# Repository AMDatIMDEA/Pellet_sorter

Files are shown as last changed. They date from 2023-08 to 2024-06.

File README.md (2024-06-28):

# Pellet distributor
CAD and Arduino/Python code files for the pellet distributor robot developed at the Accelerated Materials Discovery group from IMDEA Materials.

A tutorial for using the code is available as a [Notebook](Code/Python/Pellet_distributor_py/Example_using_pellet_distributor.ipynb)

⚠ All parts are designed to be printed, if possible, according to the specified [Cura settings](Resources/Ultimaker_S5_Cura_Config.curaprofile). These include:
- Horizontal Expansion: -0.1 mm
- Initial Layer Horizontal Expansion: -0.16 mm

## Introduction to the project & current state
The pellet distributor robot is a double-jointed articulated tube designed for pellets to be distributed into a set of cups on a tray, with the aim of automating the output of the material production process:
> Mixing of desired composition 🠚 Extrusion 🠚 Cooling 🠚 Pelletizing 🠚 **SORTING** ⇨ Transport to sample manufacture & experimentation

The parts, designed in FreeCAD, are made mostly of PLA by 3D printing, together with 50mm diameter PVC pipe sections, and nuts and bolts for fastening. The robot, measuring 552x497x236mm, uses two stepper motors for positioning, one on its base and another closer to the end of the arm, allowing it to effectively sweep a truncated circular sector below the pelletizer that covers the entire area of a tray. A third stepper actuates the opening and closing of a butterfly valve.  The whole assembly is suspended beneath the pelletizer by two arms on the top funnel/hopper, inserted into aluminum railings just under where the pellets exit. These make their way through the first joint, the valve (if open), and through the second joint, before reaching the nozzle and dropping into a cup or being discarded. The tray holding the cups is set up on a scale, which enables the control of fill levels of cups, as well as determining the material yield.

The motors are controled by A4988 drivers and an Arduino Uno R3 board, which is in turn managed by a Python script on a computer. The communication between these is established through a serial protocol, hence the Arduino must be plugged in by USB during operation, in addition to the power cable for the motors. The scale is also connected by its own serial port to the script. This Python code makes use of the Inverse Kinematics Python library (IKPy), through which the number of steps that each motor needs to take can be calculated in order for the robot to move its nozzle to a desired position. This versatility in the code, together with the fact that the arm should be able to reach any point within the swept region defined above, implies that the design is theoretically adaptable to any tray and cup arrangement, as long as these fit within said area.

The way the current script works is the following: Firstly, the robot arm must be pointing completely straight and perpendicular to the face of the pelletizer, and the current 9-hole square tray, whose center is alligned with the axis of rotation of the bottom joint, is set up on the scale. Then, the scale is zeroed, the arm rotates to the first cup's coordinates, opens the valve and lets pellets through. Once the predetermined weight capacity of each cup is reached, as measured on the scale, the script knows to close the valve and move on to the next cup. It does this rotating through all 8 external cups, then finally goeas to the center cup. Once this one has been filled it returns to the initial position.

The following items are currently hard-coded into the script, hence they are accounted for but require user input if change is needed:
- Initial position of the robot arm's tip
- Position of the tray relative to the robot
- Position of each cup relative to the tray
- Occupancy state of the tray slots
- Cup fill level, material, and other properties

However, the following are addressed dynamicaly, and therefore would require no adaptation in case of future tray design and operation changes:
- Path to take in between coordinates
- Operation of the valve
- Operation of the scale
- The Arduino code as a whole

## Current issues and future development
There are, however, to problems that have been encountered with this design. First, the flexing of the mounting bracket of the top stepper motor, together with the fact that the top joint is driven by a gear train instead of a belt mechanism, means that during translation of the top arm (which currently only occurs for the 9th cup) the gears can be pushed appart under torque and disengaged by the flexing, resulting in missed rotation. Note that, since there is no feedback through the motors themselves nor through an external system such as CV, the script has no way of accounting for missed steps, or, as is the case here, a disengagement of the gear train, hence it can be mistaken about the real location of the nozzle.

A second issue is static charge. It appears that most stages of the material production process can induce it: the extrusion by the fillament rubbing at the exit; the cooling channel again by triboelectric effect due to the air sprayed over the fillament; the pelletizer also by contact, with the rollers or the casing; and even perhaps the robot tube itself once the pellets are cut, since they slide over the plastic surface. This causes problems since it allows for two things to happen: the pellets might get stuck in the tube due to attraction to the walls; and, once a cup reaches a certain fill level, the charged pellets within it act as an electric repulsor for oncoming pelles (since they all hold the same charge), pushing them away from falling into the cup and in some instances making them fly out of the cup rather dramatically. I believe that simply discharging the pellets, as has been attempted, is not a sufficient fix since they might be attracted to the discharge points (Eg: aluminum foil), creating an insulating barrier through which the rest of the pellets cannot lose their charge, hence the problem remains. The current consideration is using ionized air, as appears to be the industry consensus, to remove the pellets charge.

In light of these hurdles, and keeping the ambitions of the whole RobotLab in mind, there are some suggestions to be made for future developments regarding this project:
- Implementing Computer Vision (CV), for direct object detection as well as asisted, for instance, through ArUco markers. This could enable:
  - Knowledge of the tray's exact coordinates, removing the need for precise alignment when placing it under the robot.
  - Determining the location of each cup individually, instead of having to hard-code their coordinates relative to the tray for each existing tray design.
  - Detecting the state of the cups, such as their fill level; or if there is a problem, so that they can be skipped (Eg: Cup missing, already full, contaminated or partially containing a material different than the one currently being extruded)
  - Interaction with a separate robotic arm, that can pick up the cups and/or trays after they have been filled.
  - Vissual feedback on the robot arm's pose, which eliminates missmatch issues between the real pose and the ideal one.
- Creating a database that, interacting with the script, can cataloge the available trays, those in storage; the contents, fill level,s and properties of every cup, etc. This would be necessity if there ever is the desire to scale production, and would be useful for the transport system to interact with.

And some less impactful TO-DOs:
- Implementing tray swapping into the script, so that after operation it holds the valve closed in the initial position while a human/robot picks up the full tray and swaps in a new, empty one. This could be done either with a simple user input through consol, which would replace restarting the script, or even in a more automatic fashion by using the scale to detect negative weight when the tray has been taken out, then waiting for a slight increase corresponding to the new empty tray being placed.
- Vertically integrating the script upwards with an overarching material production control script, that manages the mixing, extrusion and pelletizing. This would not be too difficult given how the robot operation is built on a functional basis, and the management of cups and trays is object-oriented.

[> Back to top](#TOP)

## Useful links & references

- [ ] [Arduino & Breadboard wiring diagram](https://github.com/AMDatIMDEA/Pellet_sorter/blob/3199d7dc5ab3ea5f197367ed4c28cb93c2f82943/Schematics/Electronics/Pellet%20Sorter%20Arduino%20and%20Driver%20Wiring%20Drawing%20Final%20Annotated.png)

### ⚡ Stepper Motors
- [Arduino AccelStepper Class Reference](https://www.airspayce.com/mikem/arduino/AccelStepper/classAccelStepper.html)
- [Arduino AccelStepper Examples](https://www.airspayce.com/mikem/arduino/AccelStepper/examples.html)
- [A4988 Driver simplified guide](https://lastminuteengineers.com/a4988-stepper-motor-driver-arduino-tutorial/)
- [ ] [Small stepper datasheet](https://github.com/AMDatIMDEA/Pellet_sorter/blob/d0cadbf57e2ab080da146999fbca15fec0f52def/Resources/Guides_and_Datasheets/290-028-1_ts-24byj48a-25-pxw%20Stepper.pdf)
- [ ] [SX-NEMA17 Stepper datasheet](https://github.com/AMDatIMDEA/Pellet_sorter/blob/d0cadbf57e2ab080da146999fbca15fec0f52def/Resources/Guides_and_Datasheets/SX17%20NEMA17%20Stepper.pdf)
- [ ] [A4998 Driver datasheet](https://github.com/AMDatIMDEA/Pellet_sorter/blob/d0cadbf57e2ab080da146999fbca15fec0f52def/Resources/Guides_and_Datasheets/A4988-%20Driver%20Datasheet.pdf)

### 🔌 Serial port
- [Arduino Serial functions](https://www.arduino.cc/reference/en/language/functions/communication/serial/)
- [Python pySerial API Classes](https://pyserial.readthedocs.io/en/latest/pyserial_api.html)

### ⛓ Inverse Kinematics
- [IKPy GitHub Repo](https://github.com/Phylliade/ikpy)
- [IKPy Documentation](https://ikpy.readthedocs.io/en/latest/ikpy.html)

### ⚖ Balance
- [ ] [CPWplus Scale datasheet](https://github.com/AMDatIMDEA/Pellet_sorter/blob/d0cadbf57e2ab080da146999fbca15fec0f52def/Resources/Guides_and_Datasheets/CPWplus_UM_USA%20Scale.pdf)

### 🐢 TurtleBot
- [TurtleBot 4 GitHub Hardware repo](https://github.com/turtlebot/turtlebot4-hardware/tree/master/TurtleBot%204/Components)
- [ ] [TurtleBot 4 Integration Platform datasheet](https://github.com/AMDatIMDEA/Pellet_sorter/blob/c34230bc0438fd95317bfee5fad6f5a7074d98d1/Resources/Guides_and_Datasheets/TurtleBot%20Top%20Integration%20platform%20draft.pdf)

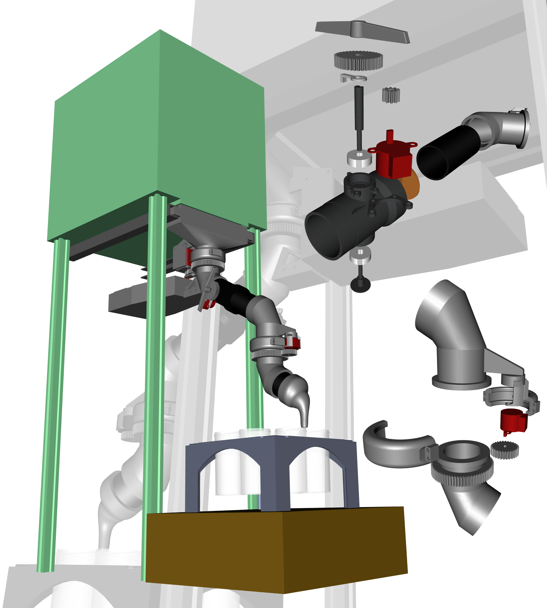
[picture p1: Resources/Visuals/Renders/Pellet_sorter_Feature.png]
Pellet sorter rendering


[> Back to top](#TOP)

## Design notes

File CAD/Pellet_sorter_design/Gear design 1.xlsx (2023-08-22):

Small stepper |  |  |  |  |  |  |  | SX17 Stepper |  |  |  |  |  |  |  | Small stepper
Module | m | 1.5 | mm |  |  |  |  | Module | m | 1.5 | mm |  |  |  |  | Module | m | 1 | mm
# Teeth G | N_G | 48 | - | Diam. G | d_G | 72 | mm | # Teeth G | N_G | 48 | - | Diam. G | d_G | 72 | mm | # Teeth G | N_G | 39 | - | Diam. G | d_G | 39 | mm
# Teeth p | N_p | 20 | - | Diam. P | d_p | 30 | mm | # Teeth p | N_p | 42 | - | Diam. P | d_p | 63 | mm | # Teeth p | N_p | 10 | - | Diam. P | d_p | 10 | mm
Ratio | i | 2.4 | - | C2C dist. | C | 51 | mm | Ratio | i | 1.142857143 | - | C2C dist. | C | 67.5 | mm | Ratio | i | 3.9 | - | C2C dist. | C | 24.5 | mm
 |  |  |  |  |  |  |  |  |  |  |  |  |  |  |  |  |  |  |  |  |  | 24.4658
 |  |  |  |  |  |  |  |  |  |  |  |  |  |  |  |  |  |  |  |  | Rescale | 0.9986040816
 |  |  |  |  |  |  |  |  |  |  |  |  |  |  |  | 0.9986040816
 |  |  |  |  |  |  |  | Scrapped: SX17 Stepper w/Idler
 |  |  |  |  |  |  |  | Module | m | 1.5 | mm
 |  |  |  |  |  |  |  | # Teeth G | N_G | 48 | - | Diam. G | d_G | 72 | mm
 |  |  |  |  |  |  |  | # Teeth p | N_p | 10 | - | Diam. P | d_p | 15 | mm | Small stepper Chute Joint update
 |  |  |  |  |  |  |  | # Teeth I | N_I | 16 | - | Diam. I | d_I | 24 | mm | Module | m | 1 | mm
 |  |  |  |  |  |  |  |  |  |  |  |  |  |  |  | # Teeth G | N_G | 72 | - | Diam. G | d_G | 72 | mm
 |  |  |  |  |  |  |  |  |  |  |  |  |  |  |  | # Teeth p | N_p | 30 | - | Diam. P | d_p | 30 | mm
 |  |  |  |  |  |  |  | Ratio | i | 4.8 | - | C2C d. GI | C_GI | 48 | mm | Ratio | i | 2.4 | - | C2C dist. | C | 51 | mm
 |  |  |  |  |  |  |  |  |  |  |  | C2C d. Ip | C_Ip | 19.5 | mm
 |  |  |  |  |  |  |  |  |  |  |  | C2C d. tot | C_tot | 67.5 | mm
 |  |  |  |  |  |  |  |  |  |  |  |  |  | 67.5
Top redisign
Module | m | 1 | mm
# Teeth G | N_G | 72 | - | Diam. G | d_G | 72 | mm
# Teeth p | N_p | 12 | - | Diam. P | d_p | 12 | mm
# Teeth I | N_I | 26 | - | Diam. I | d_I | 26 | mm
Ratio | i | 6 | - | C2C d. GI | C_GI | 49 | mm
 |  |  |  | C2C d. Ip | C_Ip | 19 | mm
 |  |  |  | C2C d. tot | C_tot | 68 | mm
 |  |  |  |  |  | 67.5

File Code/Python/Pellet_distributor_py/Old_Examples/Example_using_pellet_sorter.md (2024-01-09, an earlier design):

# Example using pellet sorter

This notebook contains an example of how to run the code for collecting the material. Most cells can be run without any modification if the collector has been built without design modifications. The lines that need modifications are markedlike this:

`###############################################################################################################`

```python
# Import Libraries
import serial
import numpy as np
import time
import os
import serial.tools.list_ports
```

In this cell, we define the port name for the arduino and the balance. We do it by listing the connected ports and selecting the ones whose device serial is the corresponding to our device. You should find the serial of your devices and change it accordingly. You can do it by inspecting the devices detected by serial.tools.list_ports.comports(). In case of doubt, try disconnecting and connecting to see which ports are affected.

```python
ports = serial.tools.list_ports.comports()

###############################################################################################################

arduino_serial = "write_here_your_arduino_serial"
balance_serial = "write_here_your_balance_serial"

###############################################################################################################

for port in ports:
    if port.serial_number == arduino_serial:
        arduino_port = port.device
    elif port.serial_number == balance_serial:
        balance_port = port.device
        
### Serial initialization
## Arduino
arduino = serial.Serial(arduino_port, 9600)
## Balance
balance = serial.Serial(balance_port, 9600)
```

We import the functions from the pellet_sorter.py script. Note: you need to install the `ikpy` library

```python
import pellet_sorter as ps
```

Define the capacity of the cup in kg

```python
###############################################################################################################
cup_capacity = 0.16
###############################################################################################################
```

The next cell defines a series of parameters needed for the calculations. They don't have to be modified unless you have modified something in the design.

```python
### Initializations
# sorter_chain, sorter_parameters and arduino should be global variables

n_joints = 2
sorter_parameters = [{'steps_in_rotation':0,'gear_ratio':0,'length_mm':0,'bound_rad':0, 'cartesian':[0,0]} for k in range(n_joints)]
## Top
sorter_parameters[0]['steps_in_rotation'] = np.round(200*1.1)   # Calibrate multiplicative factor to compensate lost steps if necessary
sorter_parameters[0]['gear_ratio'] = 6
sorter_parameters[0]['length_mm'] = 180.5
sorter_parameters[0]['bound_rad'] = np.deg2rad(35)    # np.deg2rad(35)  # IK Rotation bound in either direction, not total
sorter_parameters[0]['cartesian'] = [sorter_parameters[0].get('length_mm'), 0]
## Bot
sorter_parameters[1]['steps_in_rotation'] = 812
sorter_parameters[1]['gear_ratio'] = 2.4
sorter_parameters[1]['length_mm'] = np.sqrt(32.7**2 + 79.2**2)  # 84.4
sorter_parameters[1]['bound_rad'] = np.deg2rad(10*360)
sorter_parameters[1]['cartesian'] = [sorter_parameters[1].get('length_mm'), 0]

# Positions of the cups in the tray

tray_1 = ps.Tray('1', [sorter_parameters[0]['length_mm'], 0], [
    ps.Slot([79.2,32.7]),
    ps.Slot([32.7,79.2]),
    ps.Slot([-32.7,79.2]),
    ps.Slot([-79.2,32.7]),
    ps.Slot([-79.2,-32.7]),
    ps.Slot([-32.7,-79.2]),
    ps.Slot([32.7,-79.2]),
    ps.Slot([79.2,-32.7]),
    ps.Slot([0,0]), 
    ])

tray_1.fill_all_slots_ez(0, cup_capacity)
tray_1.set_all_material('PLA####')
```

In the next cell, we use the Arduino Command Line Interface (arduino-cli) to compile and upload the arduino script. If you prefer to do it using the Graphical User Interface, skip this cell. For using it, update the location of your arduino-cli

```python
###############################################################################################################

os.system("/PATH/arduino-cli compile --fqbn arduino:avr:uno ../../Arduino/Pellet_sorter_v2/Pellet_sorter_v2.ino")
os.system("/PATH/arduino-cli upload -p "+arduino_port+" --fqbn arduino:avr:uno ../../Arduino/Pellet_sorter_v2/Pellet_sorter_v2.ino")

###############################################################################################################
```

The `fill_tray` function will run all the process. It uses the objects defined in the previous steps. The three parameters that allow interesting customization are: 

`:param seq: List with the order of filling of the cups. If None, they will all be filled in default order`

`:param purge_slot: Number of the slot used for purging. This slot can be left without cup so the material is discarded. Used when changing material. If None, no purging will be done.`
                        
`:param purge_time: Time for purge in minutes. Default: 0`

If `seq = None` and `purge_slot = None`, the cups will be filled sequentially (from 0 to 8) without any purging.

If `purge_slot` is not None, like `purge_slot = 0` for example, that hole will be used for purging. That hole should be left empty (without cup), and the tray should be in some kind of box or container so the pellets are not spilled everywhere. In that case, if seq is None the  purging will be made after each cup, so the cup 1 will be filled, then purge, then cup 2, then purge, etc.

For more detailed control, you can use `seq`. For example, if you want cups 1 and 2 filled with one material and cups 3 and 4 with another, you can use `purge_slot = 0` and `seq = [1,2,0,3,4,0]`. In this way, after filling cups 1 and 2 with the same material it will make a purge in slot 0, and the fill cups 3 and 4. 

```python
##################################################################################################################

ps.fill_tray(tray_1, sorter_parameters, arduino, balance, seq = None, purge_slot = 0, purge_time = 1)

###############################################################################################################
```

NOTE: As an alternative, you can use `fill_tray_SIMULATED` to check if the filling order is the desired

```python

ps.fill_tray_SIMULATED(tray_1, sorter_parameters, seq = None, purge_slot = 7, purge_time = 1)
```

```python

```

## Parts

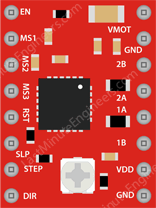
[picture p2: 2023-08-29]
Schematics/Electronics/Components/A4988-Stepper-Motor-Driver.png

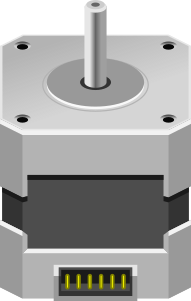
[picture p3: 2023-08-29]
Schematics/Electronics/Components/NEMA 17.png

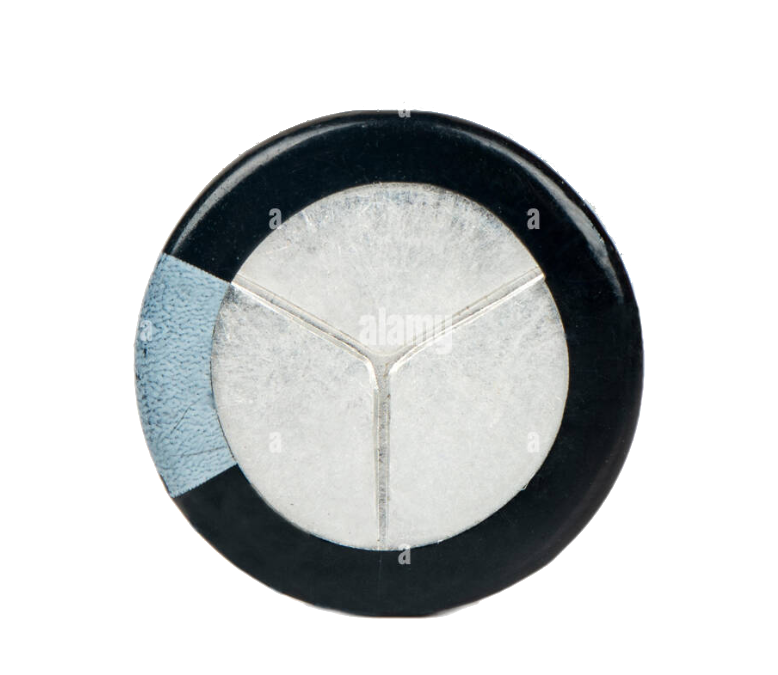
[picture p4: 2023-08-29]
Schematics/Electronics/Components/Capacitor_top.PNG

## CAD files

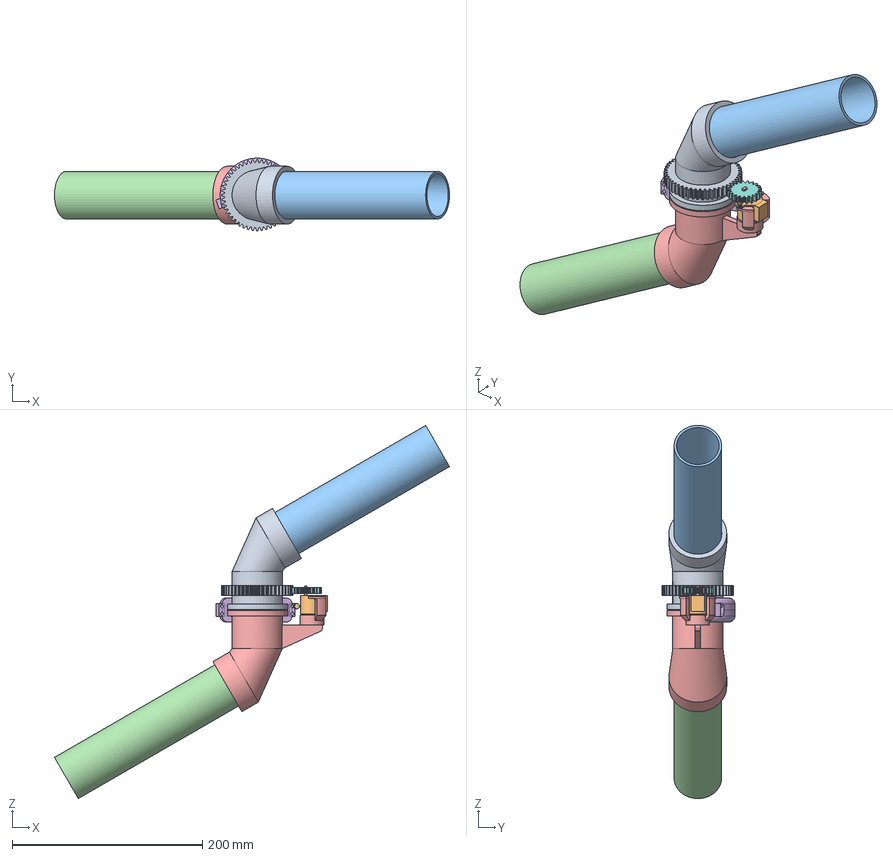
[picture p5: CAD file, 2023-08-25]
CAD/Pellet_sorter_design/Pellet Sorter chute joint.FCStd
414.9 x 76.4 x 391.9 mm
Body: Top
Body002: Motor
Body003: Pipe top
Body003: Pipe bottom
Body: Bottom
Body008: Half clamp003
Body009: Screw (M3 cut)001
Body011: Pinion V1

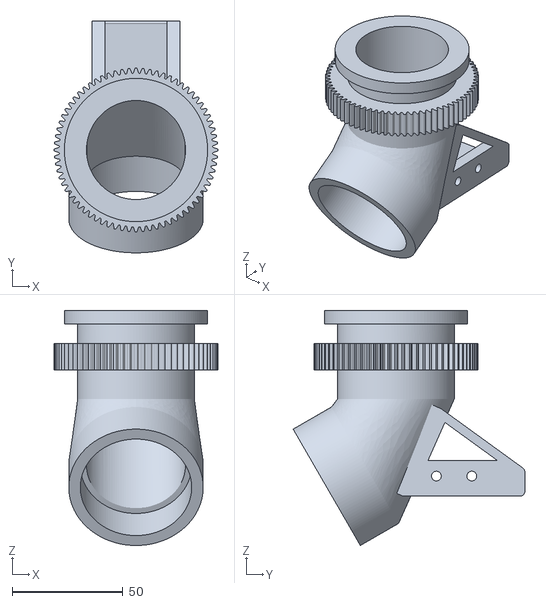
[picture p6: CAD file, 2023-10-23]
STL/Elbow1.stl
74.0 x 104.8 x 106.3

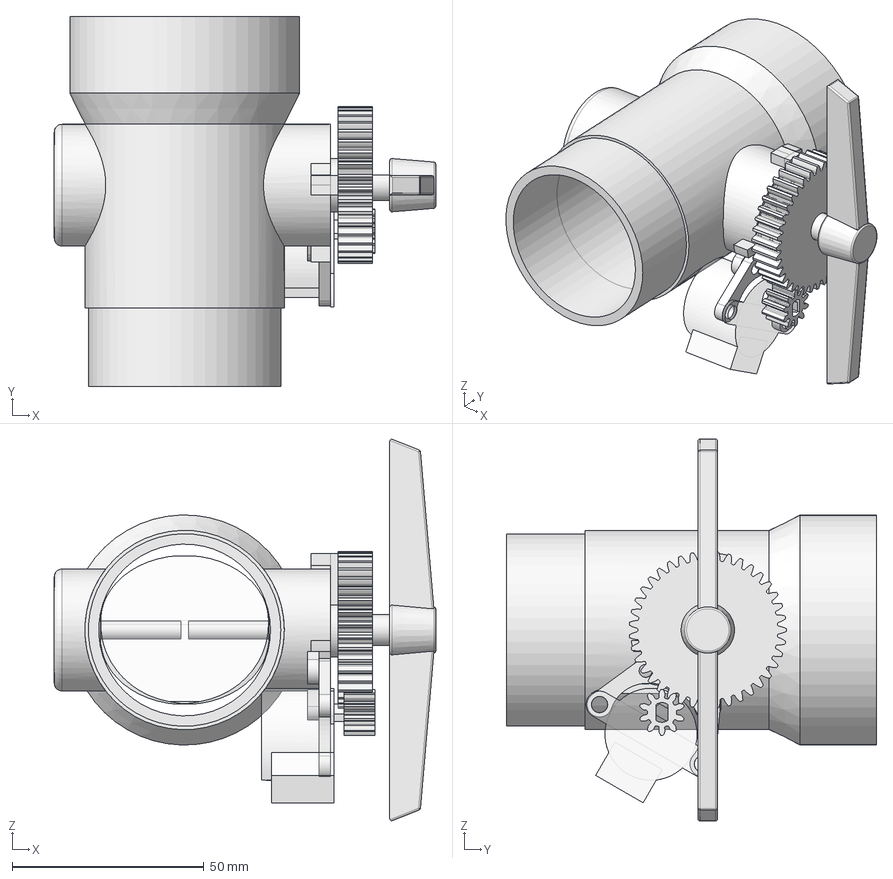
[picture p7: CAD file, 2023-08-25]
CAD/Pellet_sorter_design/Pellet Sorter butterfly valve.FCStd
99.5 x 96.5 x 99.5 mm
Body: Butterfly v0
Body002: Shaft v0
Body002: Bearing
Body002: Pin v0
Body006: Ball stop
Body002: Motor
Body009: Gear v001
Body005: Handle
Body014: Housing v0
Body008: Motor link v001
Body008: Pinion v002

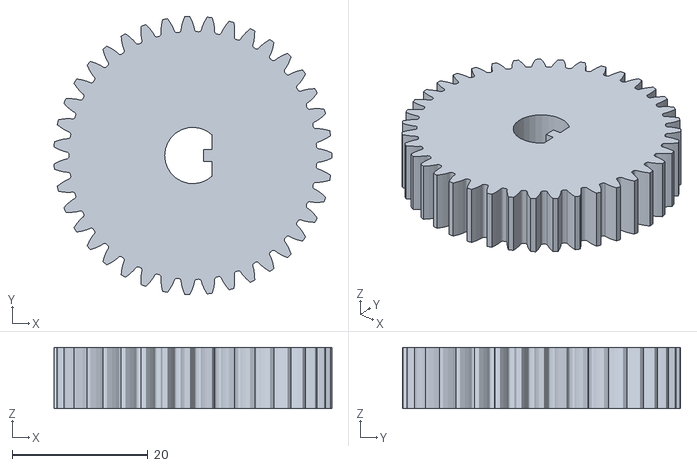
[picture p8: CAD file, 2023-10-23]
STL/Gear.stl
41.0 x 41.0 x 9.00

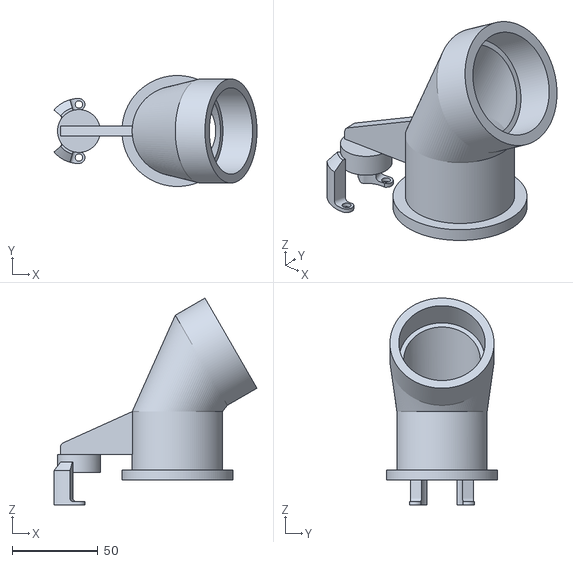
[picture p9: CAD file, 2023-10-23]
STL/Elbow2.stl
118.6 x 64.8 x 120.8

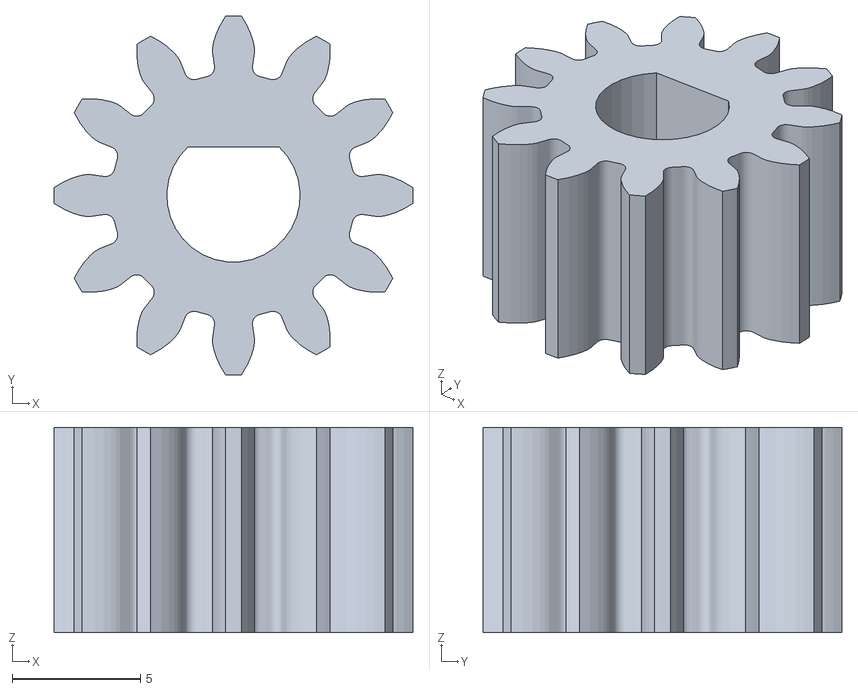
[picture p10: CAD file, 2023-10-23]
STL/1mmPinion.stl
14.0 x 14.0 x 8.00

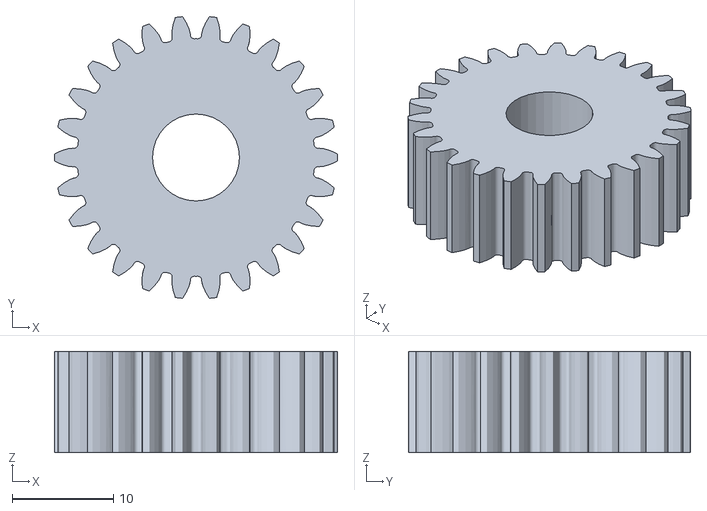
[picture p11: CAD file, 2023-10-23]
STL/1mmIdler.stl
28.0 x 27.9 x 10.0

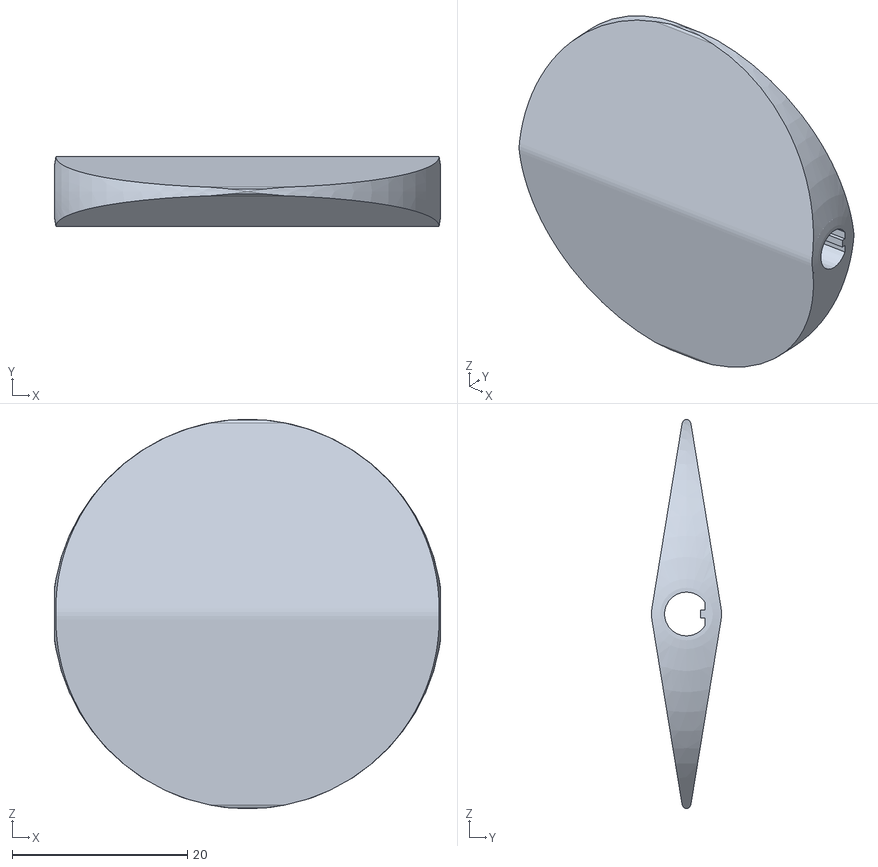
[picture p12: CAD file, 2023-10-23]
STL/Disc.stl
44.0 x 7.99 x 44.4

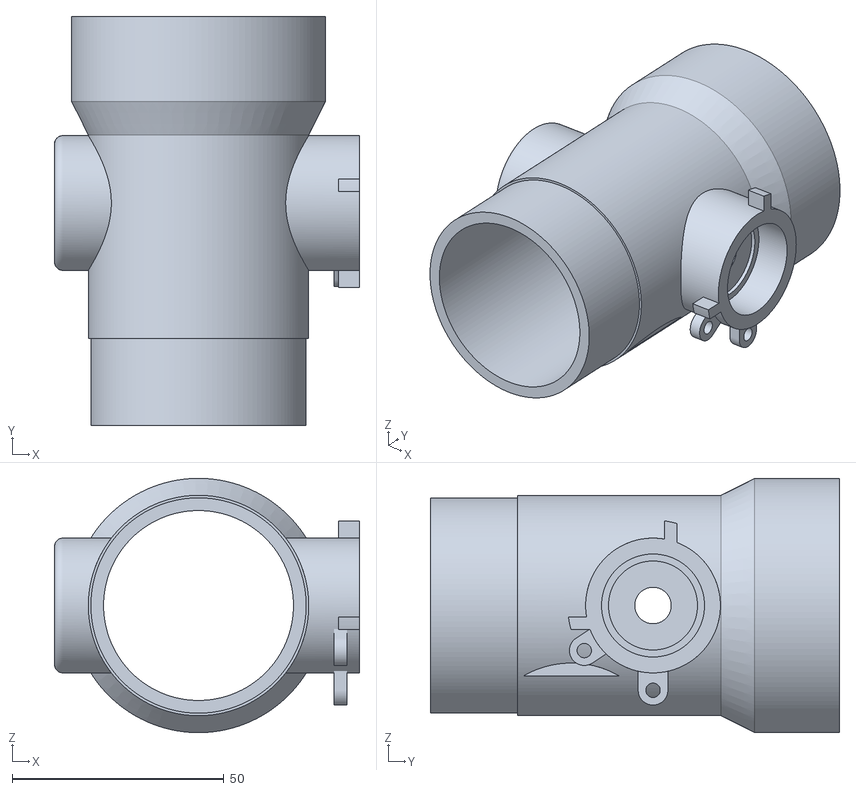
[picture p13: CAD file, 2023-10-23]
STL/ValveHousing.stl
72.0 x 96.5 x 60.0

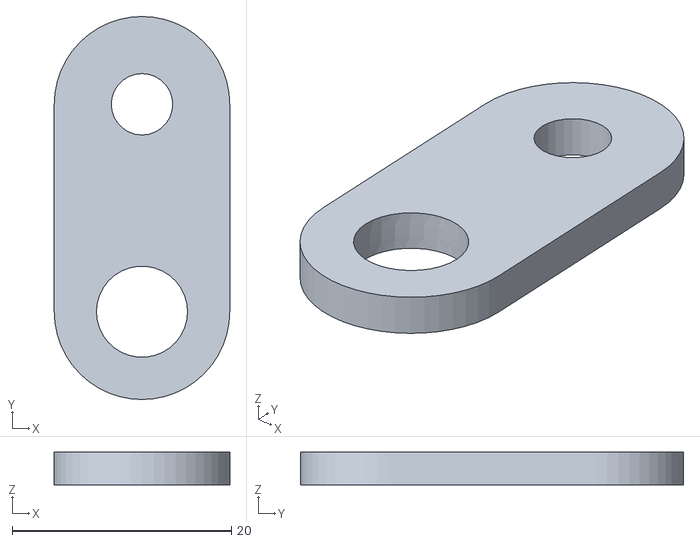
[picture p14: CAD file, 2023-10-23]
STL/IdlerCap.stl
16.0 x 34.9 x 3.00

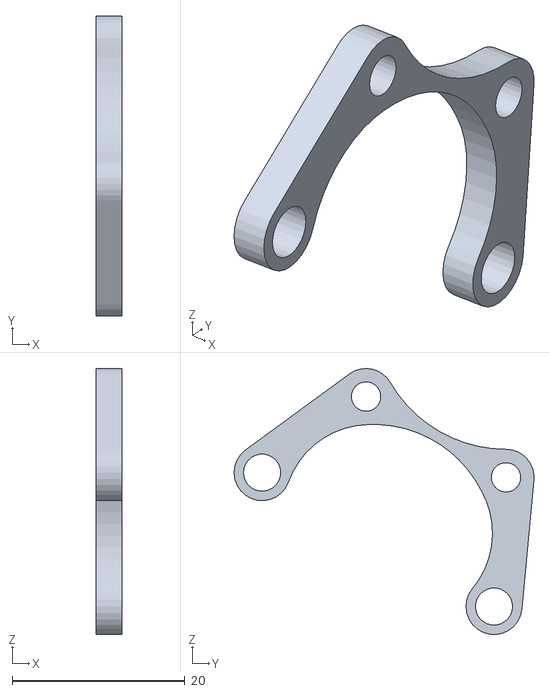
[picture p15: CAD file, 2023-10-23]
STL/MotorLink.stl
3.00 x 34.7 x 30.8

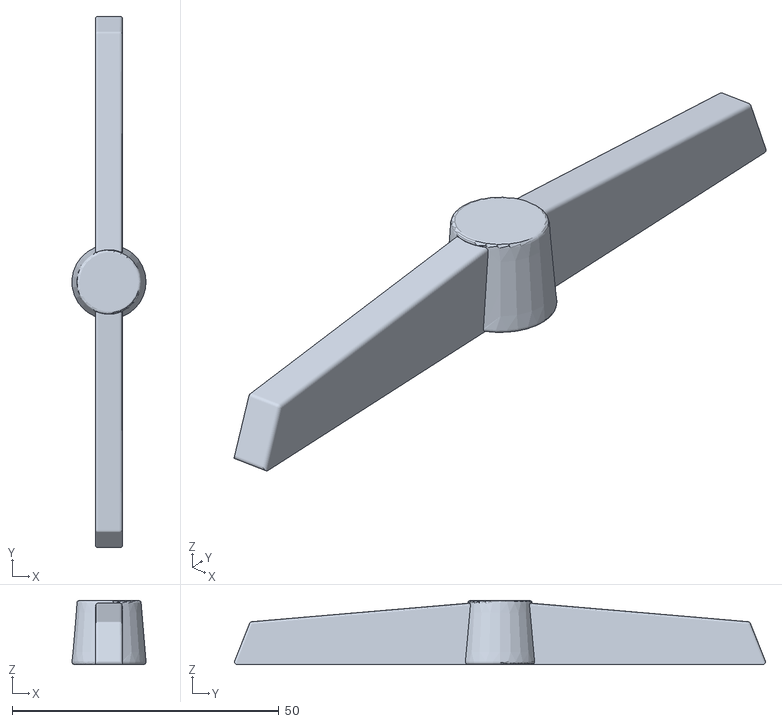
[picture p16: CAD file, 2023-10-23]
STL/Handle.stl
13.9 x 99.5 x 12.0

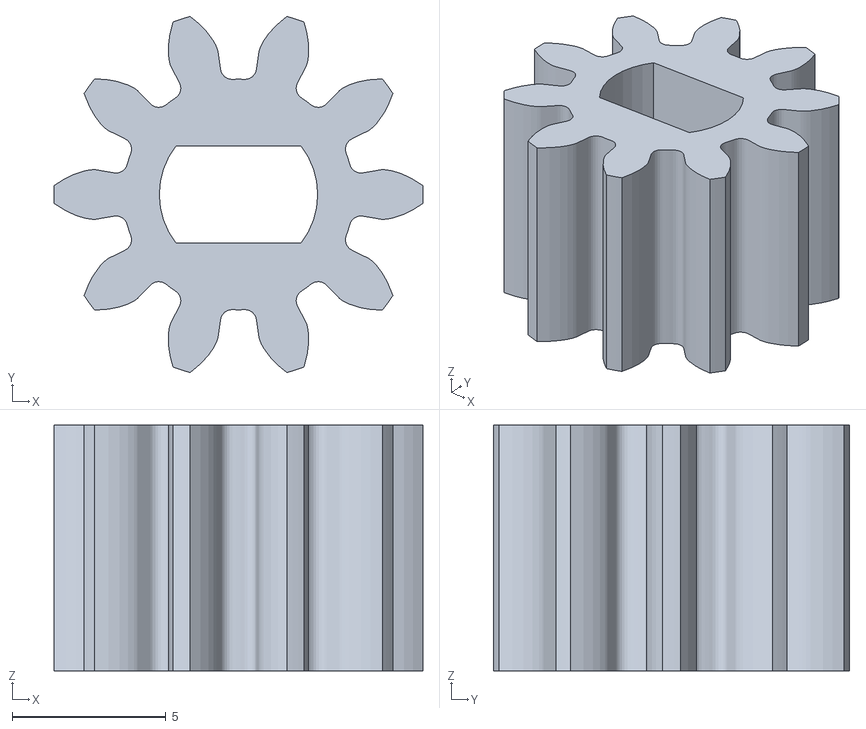
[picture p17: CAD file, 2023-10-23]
STL/ValvePinion.stl
12.0 x 11.6 x 8.00

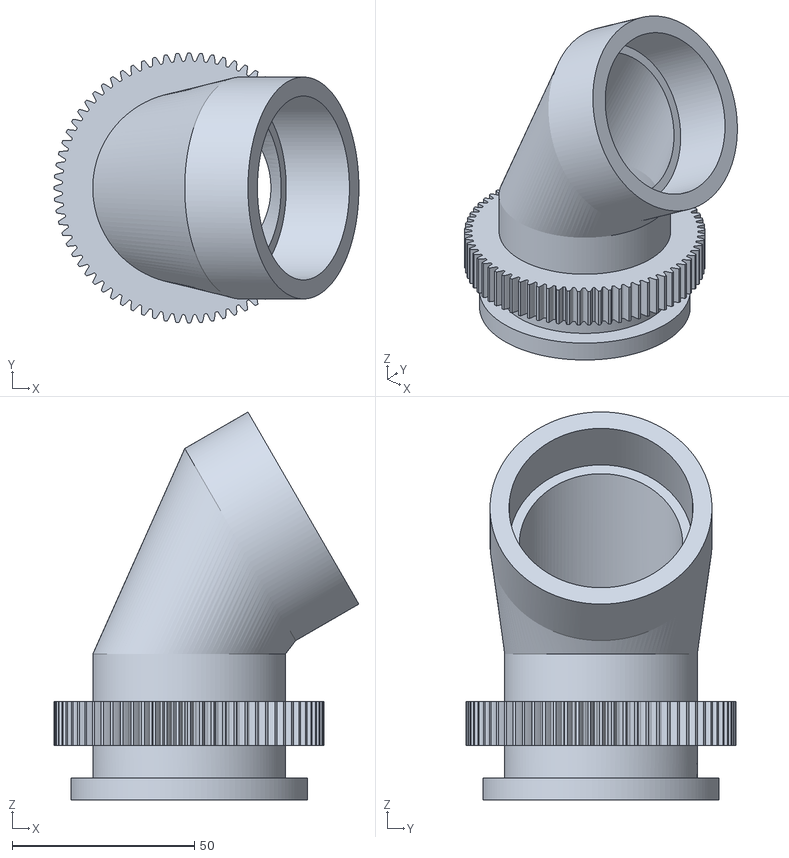
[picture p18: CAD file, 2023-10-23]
STL/Elbow3.stl
83.5 x 74.0 x 106.3

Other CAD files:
STL/Shaft.stl
STL/CircuitCase.stl
STL/JointPinion.stl
STL/NemaMount.stl
CAD/Pellet_sorter_design/Deprecated/Pellet Sorter ball valve.FCStd
CAD/Pellet_sorter_design/Deprecated/Pellet Sorter top joint v0.FCStd
STL/BallStop.stl
STL/Cover.stl
STL/HalfClamp.stl
STL/IdlerLink.stl
STL/Nozzle.stl
STL/Pin.stl
STL/TopFunnel.stl

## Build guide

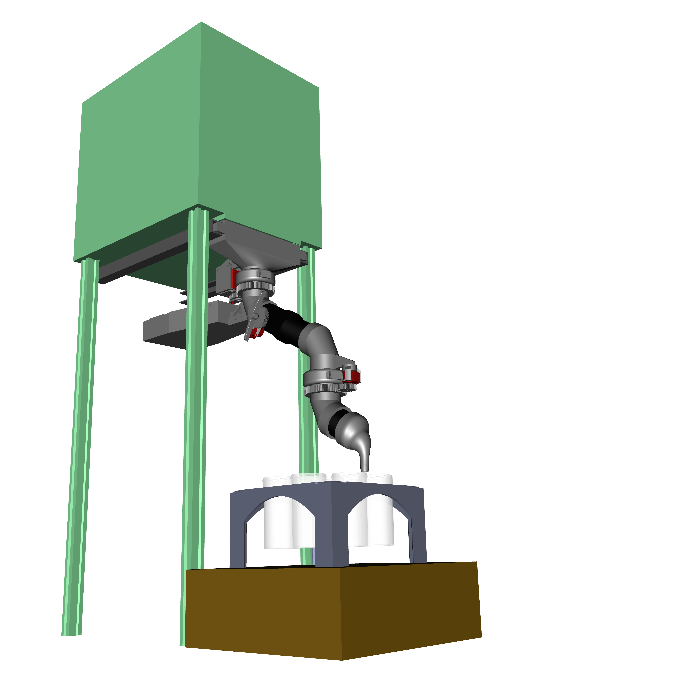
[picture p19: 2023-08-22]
Resources/Visuals/Renders/Pellet_sorter_Assembly_view_Full.png

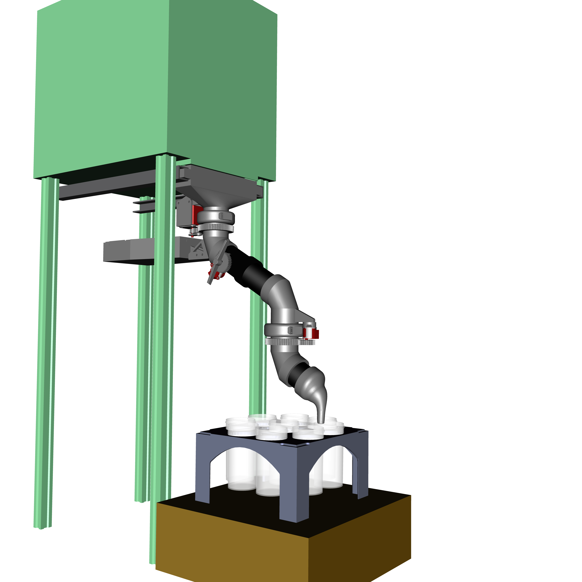
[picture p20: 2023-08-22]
Resources/Visuals/Renders/Pellet_sorter_Assembly_view.png

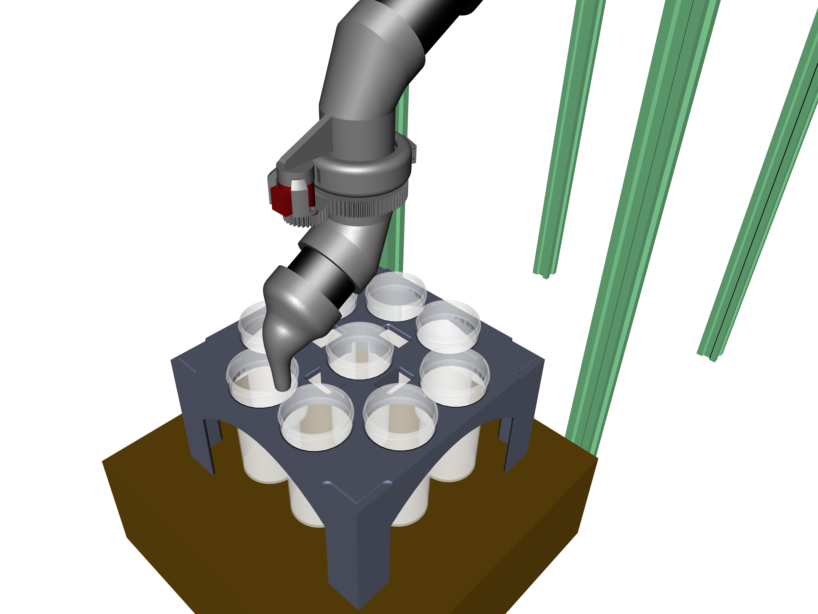
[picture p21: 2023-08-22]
Resources/Visuals/Renders/Pellet_sorter_Assembly_view_Tray.png

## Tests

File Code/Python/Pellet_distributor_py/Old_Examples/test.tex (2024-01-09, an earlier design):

\section{Example using pellet sorter}\label{example-using-pellet-sorter}

This notebook contains an example of how to run the code for collecting
the material. Most cells can be run without any modification if the
collector has been built without design modifications. The lines that
need modifications are markedlike this:

\passthrough{\lstinline!\#\#\#\#\#\#\#\#\#\#\#\#\#\#\#\#\#\#\#\#\#\#\#\#\#\#\#\#\#\#\#\#\#\#\#\#\#\#\#\#\#\#\#\#\#\#\#\#\#\#\#\#\#\#\#\#\#\#\#\#\#\#\#\#\#\#\#\#\#\#\#\#\#\#\#\#\#\#\#\#\#\#\#\#\#\#\#\#\#\#\#\#\#\#\#\#\#\#\#\#\#\#\#\#\#\#\#\#\#\#\#!}

\begin{lstlisting}[language=Python]
# Import Libraries
import serial
import numpy as np
import time
import os
import serial.tools.list_ports
\end{lstlisting}

In this cell, we define the port name for the arduino and the balance.
We do it by listing the connected ports and selecting the ones whose
device serial is the corresponding to our device. You should find the
serial of your devices and change it accordingly. You can do it by
inspecting the devices detected by serial.tools.list\_ports.comports().
In case of doubt, try disconnecting and connecting to see which ports
are affected.

\begin{lstlisting}[language=Python]
ports = serial.tools.list_ports.comports()

###############################################################################################################

arduino_serial = "write_here_your_arduino_serial"
balance_serial = "write_here_your_balance_serial"

###############################################################################################################

for port in ports:
    if port.serial_number == arduino_serial:
        arduino_port = port.device
    elif port.serial_number == balance_serial:
        balance_port = port.device
        
### Serial initialization
## Arduino
arduino = serial.Serial(arduino_port, 9600)
## Balance
balance = serial.Serial(balance_port, 9600)
\end{lstlisting}

We import the functions from the pellet\_sorter.py script. Note: you
need to install the \passthrough{\lstinline!ikpy!} library

\begin{lstlisting}[language=Python]
import pellet_sorter as ps
\end{lstlisting}

Define the capacity of the cup in kg

\begin{lstlisting}[language=Python]
###############################################################################################################
cup_capacity = 0.16
###############################################################################################################
\end{lstlisting}

The next cell defines a series of parameters needed for the
calculations. They don't have to be modified unless you have modified
something in the design.

\begin{lstlisting}[language=Python]
### Initializations
# sorter_chain, sorter_parameters and arduino should be global variables

n_joints = 2
sorter_parameters = [{'steps_in_rotation':0,'gear_ratio':0,'length_mm':0,'bound_rad':0, 'cartesian':[0,0]} for k in range(n_joints)]
## Top
sorter_parameters[0]['steps_in_rotation'] = np.round(200*1.1)   # Calibrate multiplicative factor to compensate lost steps if necessary
sorter_parameters[0]['gear_ratio'] = 6
sorter_parameters[0]['length_mm'] = 180.5
sorter_parameters[0]['bound_rad'] = np.deg2rad(35)    # np.deg2rad(35)  # IK Rotation bound in either direction, not total
sorter_parameters[0]['cartesian'] = [sorter_parameters[0].get('length_mm'), 0]
## Bot
sorter_parameters[1]['steps_in_rotation'] = 812
sorter_parameters[1]['gear_ratio'] = 2.4
sorter_parameters[1]['length_mm'] = np.sqrt(32.7**2 + 79.2**2)  # 84.4
sorter_parameters[1]['bound_rad'] = np.deg2rad(10*360)
sorter_parameters[1]['cartesian'] = [sorter_parameters[1].get('length_mm'), 0]

# Positions of the cups in the tray

tray_1 = ps.Tray('1', [sorter_parameters[0]['length_mm'], 0], [
    ps.Slot([79.2,32.7]),
    ps.Slot([32.7,79.2]),
    ps.Slot([-32.7,79.2]),
    ps.Slot([-79.2,32.7]),
    ps.Slot([-79.2,-32.7]),
    ps.Slot([-32.7,-79.2]),
    ps.Slot([32.7,-79.2]),
    ps.Slot([79.2,-32.7]),
    ps.Slot([0,0]), 
    ])

tray_1.fill_all_slots_ez(0, cup_capacity)
tray_1.set_all_material('PLA####')
\end{lstlisting}

In the next cell, we use the Arduino Command Line Interface
(arduino-cli) to compile and upload the arduino script. If you prefer to
do it using the Graphical User Interface, skip this cell. For using it,
update the location of your arduino-cli

\begin{lstlisting}[language=Python]
###############################################################################################################

os.system("/PATH/arduino-cli compile --fqbn arduino:avr:uno ../../Arduino/Pellet_sorter_v2/Pellet_sorter_v2.ino")
os.system("/PATH/arduino-cli upload -p "+arduino_port+" --fqbn arduino:avr:uno ../../Arduino/Pellet_sorter_v2/Pellet_sorter_v2.ino")

###############################################################################################################
\end{lstlisting}

The \passthrough{\lstinline!fill\_tray!} function will run all the
process. It uses the objects defined in the previous steps. The three
parameters that allow interesting customization are:

\passthrough{\lstinline!:param seq: List with the order of filling of the cups. If None, they will all be filled in default order!}

\passthrough{\lstinline!:param purge\_slot: Number of the slot used for purging. This slot can be left without cup so the material is discarded. Used when changing material. If None, no purging will be done.!}

\passthrough{\lstinline!:param purge\_time: Time for purge in minutes. Default: 0!}

If \passthrough{\lstinline!seq = None!} and
\passthrough{\lstinline!purge\_slot = None!}, the cups will be filled
sequentially (from 0 to 8) without any purging.

If \passthrough{\lstinline!purge\_slot!} is not None, like
\passthrough{\lstinline!purge\_slot = 0!} for example, that hole will be
used for purging. That hole should be left empty (without cup), and the
tray should be in some kind of box or container so the pellets are not
spilled everywhere. In that case, if seq is None the purging will be
made after each cup, so the cup 1 will be filled, then purge, then cup
2, then purge, etc.

For more detailed control, you can use \passthrough{\lstinline!seq!}.
For example, if you want cups 1 and 2 filled with one material and cups
3 and 4 with another, you can use
\passthrough{\lstinline!purge\_slot = 0!} and
\passthrough{\lstinline!seq = [1,2,0,3,4,0]!}. In this way, after
filling cups 1 and 2 with the same material it will make a purge in slot
0, and the fill cups 3 and 4.

\begin{lstlisting}[language=Python]
##################################################################################################################

ps.fill_tray(tray_1, sorter_parameters, arduino, balance, seq = None, purge_slot = 0, purge_time = 1)

###############################################################################################################
\end{lstlisting}

NOTE: As an alternative, you can use
\passthrough{\lstinline!fill\_tray\_SIMULATED!} to check if the filling
order is the desired

\begin{lstlisting}[language=Python]

ps.fill_tray_SIMULATED(tray_1, sorter_parameters, seq = None, purge_slot = 7, purge_time = 1)
\end{lstlisting}

\begin{lstlisting}[language=Python]
\end{lstlisting}

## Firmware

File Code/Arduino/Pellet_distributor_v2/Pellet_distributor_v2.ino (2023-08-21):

#include <AccelStepper.h>
#include <ctype.h>
#include <string.h>

// Pin and stepper definitions
// Tube joints
const int STEP_PIN_TOP = 3;
const int DIRECTION_PIN_TOP = 2;
const int STEP_PIN_BOT = 6;
const int DIRECTION_PIN_BOT = 5;
const int SLEEP_PIN_TOP = 4;
const int SLEEP_PIN_BOT = 7;
AccelStepper stepperTop(AccelStepper::DRIVER, STEP_PIN_TOP, DIRECTION_PIN_TOP); // (Driver default has step_pin = 2, direction_pin = 3)
AccelStepper stepperBot(AccelStepper::DRIVER, STEP_PIN_BOT, DIRECTION_PIN_BOT); // (Driver default has step_pin = 2, direction_pin = 3)
// Valve
const int STEP_PIN_VALVE = 9;
const int DIRECTION_PIN_VALVE = 8;
const int SLEEP_PIN_VALVE = 10;
AccelStepper stepperValve(AccelStepper::DRIVER, STEP_PIN_VALVE, DIRECTION_PIN_VALVE); // (Driver default has step_pin = 2, direction_pin = 3)


// Kinematic definitions
const int accel = 500;
// Tube joints
const int max_speed_top = 100;
const int max_speed_bot = 200;
const int dir_top = -1; // Switch between 1 and -1 to reverse stepper directions
const int dir_bot = 1;
// Valve
const int max_speed_valve = 260;
const int steps_valve = 792; // 3.9*812/4

// Serial signal definitions
// Tube joints
const int stepper_number = 2;
const int number_size = 5;
const int signal_size = stepper_number*number_size;
String signal = "";  // Signal consists of 10 chars, 5 for each stepper, with format sddddsdddd where s is sign (0 or -) and d are the digits. Positive means CCW from top view.
String signal_empty = "";
// Valve
const int valve_signal_size = 2;
String valve_signal_list = "v01"; // v0 closes valve, v1 opens valve

// Others
boolean running_top = false;
boolean running_bot = false;
boolean running_valve = false;

void setup() {
// put your setup code here, to run once:
  Serial.begin(9600);

  stepperTop.setMaxSpeed(max_speed_top);
  stepperTop.setAcceleration(accel);
  stepperBot.setMaxSpeed(max_speed_bot);
  stepperBot.setAcceleration(accel);

  stepperValve.setMaxSpeed(max_speed_valve);
  stepperValve.setAcceleration(accel);

  for (int i = 0; i < signal_size; i++) {
    signal.concat(0);
  }
  signal_empty = signal;

  pinMode(SLEEP_PIN_TOP, OUTPUT);
  pinMode(SLEEP_PIN_BOT, OUTPUT);
  pinMode(SLEEP_PIN_VALVE, OUTPUT);

  DriverSleep(SLEEP_PIN_TOP);
  DriverSleep(SLEEP_PIN_BOT);
  DriverSleep(SLEEP_PIN_VALVE);
}


void loop() {
// put your main code here, to run repeatedly:
  stepperTop.run();
  stepperBot.run();
  stepperValve.run();

  if (Serial.available() > 0) {
    signal = Serial.readString();
    signal.trim();
    if (isValidSignal(signal)){
      signalToTarget(signal);
      running_top = true;
      running_bot = true;
    }
    else if (isValidValveSignal(signal)){
      signalToValve(signal);
      running_valve = true;
    }
    signal = signal_empty;
  }

//  if (running_top && !stepperTop.isRunning()) {
//    running_top = false;
//    DriverSleep(SLEEP_PIN_TOP);
//    Serial.println("top finished");
//  }
//
//  if (running_bot && !stepperBot.isRunning()) {
//    running_bot = false;
//    DriverSleep(SLEEP_PIN_BOT);
//    Serial.println("bot finished");
//  }

  if (running_top && running_bot && !stepperTop.isRunning() && !stepperBot.isRunning()) {
    running_top = false;
    running_bot = false;
    DriverSleep(SLEEP_PIN_TOP);
    DriverSleep(SLEEP_PIN_BOT);
    Serial.println("pos finished");
  }

  if (running_valve && !stepperValve.isRunning()) {
    running_valve = false;
    DriverSleep(SLEEP_PIN_VALVE);
    Serial.println("val finished");
  }
}


void newTarget(int steps_top, int steps_bot){
// Sets target position to specified number of steps
  DriverWakeUp(SLEEP_PIN_TOP);
  DriverWakeUp(SLEEP_PIN_BOT);
  // Serial.println("Updated target");
  stepperTop.move(dir_top*steps_top);
  stepperBot.move(dir_bot*steps_bot);
}

void signalToTarget(String signal){
  String steps_top = signal.substring(0, number_size);
  String steps_bot = signal.substring(number_size, 2*number_size);
  newTarget(steps_top.toInt(), steps_bot.toInt());
}

boolean isValidNumber(String str){
  // if(str.length() != number_size) return false;
  if(str.charAt(0) != '0' && str.charAt(0) != '-') return false;
  for(byte i=1; i<str.length(); i++){
    if(!isDigit(str.charAt(i))) return false;
  }
  return true;
}

boolean isValidSignal(String str){
  if(str.length() != signal_size) return false;
  for (int i = 0; i < stepper_number; i++) {
    if(!isValidNumber(str.substring(i*number_size, (i+1)*number_size))) return false;
  }
  return true;
}

void DriverWakeUp(int SLEEP_PIN){
  digitalWrite(SLEEP_PIN, HIGH);
  delay(100); // Driver Datasheet: "When emerging from Sleep mode, in order to allow the charge pump to stabilize, provide a delay of 1 ms before issuing a Step command."
}

void DriverSleep(int SLEEP_PIN){
  digitalWrite(SLEEP_PIN, LOW);
}


boolean isValidValveSignal(String str){
  if(str.length() != valve_signal_size) return false;
  if(str.charAt(0) != valve_signal_list.charAt(0)) return false;
//  for (int i = 1; i < valve_signal_list.length(); i++) {
//    if(str.charAt(1) != valve_signal_list.charAt(i)) return false;
//  }
  return true;
}

void runValve(char valve_mode){
  DriverWakeUp(SLEEP_PIN_VALVE);
  if (valve_mode == valve_signal_list.charAt(1)){
    Serial.println("Closing valve");
    stepperValve.move(steps_valve);
  }
  else if(valve_mode == valve_signal_list.charAt(2)){
    Serial.println("Opening valve");
    stepperValve.move(-steps_valve);
  }
}

void signalToValve(String signal){
  runValve(signal.charAt(1));
}

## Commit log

2023-08-22 Added Acc. Conf. showcase files, Gear design Excel Sheet
    [Gear design 1.xlsx]
2023-08-22 Added guides and datasheets for steppers, driver, and scale
2023-08-24 Added Arduino libraries, TurtleBot Tray designs
2023-08-25 Upload pellet sorter design files, restructured
    [Gear design 1.xlsx, Pellet Sorter ball valve.FCStd, Pellet Sorter butterfly valve.FCStd, Pellet Sorter chute joint.FCStd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]
2023-08-29 Update design, add electronics diagram
    [Pellet Sorter Arduino and Driver Wiring TinkerCAD.brd]
2023-08-29 Fix capacitor orientation
2023-08-29 Add valve assembly images
2023-08-30 Added lower joint assembly pictures
